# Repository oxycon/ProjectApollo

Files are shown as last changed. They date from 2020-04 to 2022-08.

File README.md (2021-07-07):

# ProjectApollo
This Github repository contains Designs/docs/software/PCB for Project Apollo (open source oxygen concentrator)

For more context behind the history/goals/motivation for this project please see our coverage in Helpful Engineering blog: 
- https://www.helpfulengineering.org/projects-news/project-spotlight-apollo-oxygen-concentrator/  

<b style='color:red'>Update</b>: check out our  presentation at RespiCon 2021! 
- https://github.com/oxycon/ProjectApollo/blob/master/docs/Project%20Apollo%20RespiCon%20v11.pdf

## Apollo v2 build instructions
- https://github.com/oxycon/ProjectApollo/blob/master/prototypes/Apollo%20v2/docs/Building%20instructions%20-%20prototype%20v2.pdf 

## Why
- Ventilators need oxygen! (typical FiO2 0.4 … 0.9)
- Oxygen generation is a big problem in developing countries. 
  - No established infrastructure. 
  - Oxygen bottles are expensive
- People are already looking at alternative (local) ways for producing oxygen
## What 
- Goal of the Apollo prototype = enabling people around the world to build the prototype as fast as possible
- Focus = Simplicity and speed of build 
- Final goal = Enable people to iterate and publish their own designs in the community
## How
- Follow the published build documentation
- Buy/source the materials (check out the BOM)
- Build the prototype
- Validate O2 concentration and flow. Use a good O2 and flow sensor. 
- Think about risk analysis and assessment: template for Apollo-derived design
- Document and iterate your own design. Publish your findings to the community! 

## Target 
- Output medical grade Oxygen ideally at 93% 
- Flow rate of 1-20 liters per minute (5 l/m being standard for oxygen therapy)

## Building instructions (prototype v2)
- Achieves O2 concentration out of the box: around 45% @ 5 liters/min (enough for less-critical ventilator use cases)
- Instructables-style (step-by-step) build instructions: https://github.com/oxycon/ProjectApollo/blob/master/prototypes/Apollo%20v2/docs/Building%20instructions%20-%20prototype%20v2.pdf 
- Bill of materials: https://github.com/oxycon/ProjectApollo/tree/master/prototypes/Apollo%20v2/BOM 

## Youtube videos
- Prototype v1 (old): https://www.youtube.com/playlist?list=PL34ykrB-qW7VGt1Hwd10Zb3s1eCDftkK8 
- Prototype v2 (latest): https://www.youtube.com/playlist?list=PL34ykrB-qW7X6d74_VnCFfBaVkm8pQXZK

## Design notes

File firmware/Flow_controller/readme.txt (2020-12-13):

This folder contains code/docs for the Flow Control with Oximeter project 

Slack channel: #hardware-oximeter-closed-loop-control discussed at Helpful Engineering

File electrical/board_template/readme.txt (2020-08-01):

Board template for Apollo boards (controller, valve driver board and sensor board)

PCB design template:
- 2-layer
- PC104 SAMTEC connector (4x26) 
- 88 mm x 88 mm = 7744 sq.mm (compatible with Eagle Freeware restrictions)
- bottom 2x26 pin row used for Apollo v4, top 2x26 pin row reserved for future use

Credit: 
- Base board template derived from the PCB design of HuskySat-1 satellite developed by University of Washington in collaboration with Raisbeck Aviation High School, Quick2space, AMSAT and others

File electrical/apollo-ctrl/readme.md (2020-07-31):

This is the circuit board for the main control circuit. The basic functions are:

 * Control all valves and fans
 * Monitor sensors
 * Monitor and alert for faults

The project is described and discussed in more detail here: https://docs.google.com/document/d/1zeXxTnBCQq67ddYeBdUPdo_KXUIRMmLPwQMJQMkbk8E/

The software used is Autodesk Eagle 9.

Please make your contributions on your own branches, as it's a nightmare merging changes to these files.

Please do not use default Eagle library components, add them to the local project .LBR file before adding them to the schematic. This ensures that everybody is using the same part and gives us the flexibility to fine tune the components.

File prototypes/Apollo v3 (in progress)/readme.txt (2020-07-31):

Apollo v3

Changes:
1) Control board (firmware/software)
	- please see the latest design from ..\firmware and ..\electrical
2) improved overall pneumatics: 3/8 piping for air intake, etc. 
3) improved zeolite (finer-grade 13X zeolite 20-40 instead of 4-8)

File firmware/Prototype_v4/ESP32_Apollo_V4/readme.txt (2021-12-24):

  ESP32 Oxygen Concentrator
 ===========================
 
This software is provided "as is" for educational purposes only. 
No claims are made regarding its fitness for medical or any other purposes. 
The authors are not liable for any injuries, damages or financial losses.

Use at your own risk!

License: MIT https://github.com/oxycon/ProjectApollo/blob/master/LICENSE.txt
For more information see: https://github.com/oxycon/ProjectApollo

------------------------------------------------------------------------------------

ESP32 Arduino install Video: https://www.youtube.com/watch?v=DgaKlh081tU&time_continue=61
  - Install Arduino IDE from https://www.arduino.cc/en/Main/Software
  - File => Preferences => Sketchbook location: {parent directory of this file, containing the "Libraries" directory, such as "root\ProjectApollo\firmware\Prototype_v4"}
  - File => Preferences => Additional Boards Manager URLs: https://dl.espressif.com/dl/package_esp32_index.json
  - Tools => Board: "xxx" => Boards Manager => ESP32
  - Tools => Board: "xxx" => ESP32 Arduino => "WEMOS LOLIN32" (or "ESP32 PICO Kit" if using the PICO board)
  - Tools => Serial Monitor => Baud: 115200

Install Library:
  - TFT_eSPI
  	!!! Edit Documents\Arduino\libraries\TFT_eSPI\User_Setup.h and configure ESP32 LCD SPI pins
  - TJpg_Decoder
  - ArduinoJson

Change WIFI credentials in Secrets.h

Note: force config change
- change #define CONFIG_MAGIC in Config.h

Control and Configuration:
There is an interactive command line interface that can be used with over the serial interface or TCP port 23.
Use telnet, PuTTY from https://putty.org or nc to connect using TCP.
Use Arduino IDE "tools=>Serial Monitor" or PuTTY from https://putty.org to connect using the USB serial port.

----------------------------------------------------------------------------------------------

  The ESP32 started randomly crashing
 =====================================

/home/runner/work/esp32-arduino-lib-builder/esp32-arduino-lib-builder/esp-idf/components/freertos/queue.c:1446 (xQueueGenericReceive)- assert failed!
abort() was called at PC 0x4008939b on core 1

Backtrace: 0x4008cf60:0x3ffbe690 0x4008d191:0x3ffbe6b0 0x4008939b:0x3ffbe6d0 0x400df875:0x3ffbe710 0x400d86cc:0x3ffbe730 0x400d6053:0x3ffbe750 0x400d60b5:0x3ffbe770 0x40080f89:0x3ffbe790 0x40081d95:0x3ffbe7b0 0x40085249:0x3ffbe7d0 0x4000bfed:0x3ffb1dd0 0x4008a7f1:0x3ffb1de0 0x40089ca4:0x3ffb1e00 0x400de844:0x3ffb1e30 0x400debcf:0x3ffb1e60 0x400d8859:0x3ffb1e80 0x400d88ad:0x3ffb1ea0 0x400d89bd:0x3ffb1ec0 0x400d7f3d:0x3ffb1ee0 0x400d81b8:0x3ffb1f10 0x400d8419:0x3ffb1f30 0x400d177b:0x3ffb1f50 0x400d59e9:0x3ffb1f70 0x400d4f7d:0x3ffb1f90 0x400e0fcd:0x3ffb1fb0 0x40089675:0x3ffb1fd0

0x4008cf60: invoke_abort at /home/runner/work/esp32-arduino-lib-builder/esp32-arduino-lib-builder/esp-idf/components/esp32/panic.c line 155
0x4008d191: abort at /home/runner/work/esp32-arduino-lib-builder/esp32-arduino-lib-builder/esp-idf/components/esp32/panic.c line 170
0x4008939b: xQueueGenericReceive at /home/runner/work/esp32-arduino-lib-builder/esp32-arduino-lib-builder/esp-idf/components/freertos/queue.c line 1446
0x400dfaf5: spiTransaction at C:\Users\caavenha\AppData\Local\Arduino15\packages\esp32\hardware\esp32\1.0.4\cores\esp32\esp32-hal-spi.c line 722
0x400d86bd: SPIClass::beginTransaction(SPISettings) at C:\Users\caavenha\AppData\Local\Arduino15\packages\esp32\hardware\esp32\1.0.4\libraries\SPI\src\SPI.cpp line 135
0x400d6058: valve_update_spi() at C:\Users\caavenha\AppData\Local\Temp\arduino_build_850040\sketch\Valve.cpp line 68
0x400d60cd: set_valves(unsigned char, unsigned char) at C:\Users\caavenha\AppData\Local\Temp\arduino_build_850040\sketch\Valve.cpp line 82
0x40080f89: concentratorISR() at C:\Users\caavenha\AppData\Local\Temp\arduino_build_850040\sketch\Concentrator.cpp line 27
0x40081d95: __timerISR at C:\Users\caavenha\AppData\Local\Arduino15\packages\esp32\hardware\esp32\1.0.4\cores\esp32\esp32-hal-timer.c line 88
0x4008a5c6: vTaskEnterCritical at /home/runner/work/esp32-arduino-lib-builder/esp32-arduino-lib-builder/esp-idf/components/freertos/tasks.c line 4190
0x4008b054: xTaskResumeAll at /home/runner/work/esp32-arduino-lib-builder/esp32-arduino-lib-builder/esp-idf/components/freertos/tasks.c line 2224
0x40089ca7: xEventGroupWaitBits at /home/runner/work/esp32-arduino-lib-builder/esp32-arduino-lib-builder/esp-idf/components/freertos/event_groups.c line 428
0x400de86c: i2cProcQueue at C:\Users\caavenha\AppData\Local\Arduino15\packages\esp32\hardware\esp32\1.0.4\cores\esp32\esp32-hal-i2c.c line 1279
0x400debf7: i2cWrite at C:\Users\caavenha\AppData\Local\Arduino15\packages\esp32\hardware\esp32\1.0.4\cores\esp32\esp32-hal-i2c.c line 1621
0x400d8881: TwoWire::writeTransmission(unsigned short, unsigned char*, unsigned short, bool) at C:\Users\caavenha\AppData\Local\Arduino15\packages\esp32\hardware\esp32\1.0.4\libraries\Wire\src\Wire.cpp line 133
0x400d88d5: TwoWire::endTransmission(bool) at C:\Users\caavenha\AppData\Local\Arduino15\packages\esp32\hardware\esp32\1.0.4\libraries\Wire\src\Wire.cpp line 158
0x400d89e5: TwoWire::endTransmission() at C:\Users\caavenha\AppData\Local\Arduino15\packages\esp32\hardware\esp32\1.0.4\libraries\Wire\src\Wire.cpp line 316
0x400d7f65: Adafruit_BME280::read24(unsigned char) at C:\Users\caavenha\Documents\Arduino\libraries\Adafruit_BME280_Library\Adafruit_BME280.cpp line 316
0x400d81e0: Adafruit_BME280::readTemperature() at C:\Users\caavenha\Documents\Arduino\libraries\Adafruit_BME280_Library\Adafruit_BME280.cpp line 407
0x400d8441: Adafruit_BME280::readHumidity() at C:\Users\caavenha\Documents\Arduino\libraries\Adafruit_BME280_Library\Adafruit_BME280.cpp line 468
0x400d177f: Bme::run() at C:\Users\caavenha\AppData\Local\Temp\arduino_build_850040\sketch\BME280.cpp line 32
0x400d59ed: sensor_run() at C:\Users\caavenha\AppData\Local\Temp\arduino_build_850040\sketch\SensorManager.cpp line 89
0x400d4f81: loop() at C:\Repos\ProjectApollo\firmware\Prototype_v4\ESP32_Apollo_V4/ESP32_Apollo_V4.ino line 69
0x400e0ff5: loopTask(void*) at C:\Users\caavenha\AppData\Local\Arduino15\packages\esp32\hardware\esp32\1.0.4\cores\esp32\main.cpp line 19
0x40089675: vPortTaskWrapper at /home/runner/work/esp32-arduino-lib-builder/esp32-arduino-lib-builder/esp-idf/components/freertos/port.c line 143

It is possible that it is not safe to call the SPI from the timer ISR in Concentrator.cpp
Essentially SPI_MUTEX_LOCK(); in esp32-hal-spi.c asserts sometimes. One possiblity could be to use software SPI for the valves.

A search also revealed:
https://github.com/espressif/arduino-esp32/issues/149 : hardware SPI is slower than software SPI by maybe a factor of 3 

For the time being SPI locks need to be disabled:
C:\Users\<user>\AppData\Local\Arduino15\packages\esp32\hardware\esp32\1.0.4\cores\esp32\esp32-hal-spi.c
#define CONFIG_DISABLE_HAL_LOCKS 1

----------------------------------------------------------------------------------------------

Type help or ? to get a list of CLI commands.

led <0|1|on|off|true|false>            Set LED state
valve <n> [0|1|on|off|true|false]      Set or get valve state
valve-drivers [count]                  Number of installed DRV-8806 valve driver chips
concentrator [0|1|on|off|true|false]   Enable or disable concentrator stage
stage-duration <stage> [miliseconds]   Set or get the duration of a specifc stage
stage-durations [miliseconds] [...]    Set or get the stage durations
stage-valves <stage> [valves]          Set or get stage valve state bit-map
stage-valve-mask <mask>                Set or get bit-masks of which valves should switch during stages
oxygen                                 Get results of last oxygen sensor measurements
pressure                               Get results of last pressure sensor measurements
humidity                               Get results of last humidity sensor measurements
temperature                            Get results of last temperature sensor measurements
color                                  Get results of last color sensor measurements
errors                                 Get error log
adr-ambient [address]                  Set or get the address of the ambient humidity, temperture, pressure sensor
adr-intake [address]                   Set or get the address of the intake humidity, temperture sensor
adr-desiccant [address]                Set or get the address of the desiccant humidity, temperture sensor
adr-output [address]                   Set or get the address of the output humidity, temperture sensor
adr-in-pressure [address]              Set or get the address of the intake pressure sensor
adr-color [address]                    Set or get the address of the color sensor
adr-out-pressure [address]             Set or get the address of the output pressure sensor
data-log [0|1|on|off|true|false]       Enable or disable concentrator data logging
cycle-stats [0|1|on|off|true|false]    Enable or disable cycle stats logging
stats [0|1|on|off|true|false]          Enable or disable long term stats logging
debug [0|1|on|off|true|false]          Enable or disable debug logging
wifi-enabled [0|1|on|off|true|false]   Enable or disable WIFI on next restart
ssid                                   Set or get WIFI SSID
wifi-password                          Set or get WIFI password
wifi-ip                                Set or get fixed WIFI IP address
dns                                    Set or get fixed WIFI DNS
gateway                                Set or get fixed WIFI gateway
subnet                                 Set or get fixed WIFI subnet
time-format                            Set or get format for time representation
date-format                            Set or get format for date representation
save                                   Save current configuration to FLASH
load                                   Restore configuration from FLASH
config                                 Return configuration as JSON
data                                   Return current sensor data as JSON
ip                                     Get local-IP address
mac                                    Get MAC address
time                                   Get current time
timezone [time zone]                   Set or get the local time zone
brighness [value]                      Set or get the display brightness 0 to 100
restart                                Restart the controller
help                                   Print help
?                                      Print help

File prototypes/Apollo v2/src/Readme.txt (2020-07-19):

Please see ../../../firmware/Prototype_v2

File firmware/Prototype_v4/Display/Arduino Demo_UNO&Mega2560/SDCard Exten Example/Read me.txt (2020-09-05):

Attention:
"SDCard Exten Example" only support the Arduino UNO board,not support the Mega2560,Because they use different SPI bus.

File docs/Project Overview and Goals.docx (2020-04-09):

Project Apollo Project Overview

DIY Oxygen Concentrator Project

Author: Adi Oltean, Jack Gallagher, Eric H Revision: 22nd March 2020

Working copy available at: https://drive.google.com/drive/folders/1AWvZsK41v0T8z20f_-QFAzTxI99lZbBv?ths=true

Goal 2

Justification 2

Assumptions 2

Project Timeline 2

Requirements 3

Useful links 3

Goal

The goal is to create extremely detailed DIY instructions for the creation of an Open Source Oxygen Concentrator. This should be concise and clear so it can be followed by those with little to no previous experience in building these types of systems.

The target price is less than $100 although this may be infeasible once development and prototypes are created.

Justification

- In the Helpful Engineering Round 1 Peer review this project was ranked 14th out of 26

proposals to make it to that stage. - It was ranked in the top 5 of the hardware projects. - It was ranked by Anaesthesiologists as “Hugely important” with a comment of “Lack of

O2 pipeline supply”

Assumptions

Note: Any assistance confirming or denying any assumptions would be appreciated as expert knowledge has not been available to date.

- Access to oxygen-rich air is critical to many medical facilities across the globe given that

we are running out of beds in many affected areas by COVID-19 [1], [2] - Additionally, according to the interviewed Seattle doc, 2⁄3 of hospitalized patients didn’t require much more care than o2 therapy, so any way to rapidly scale out concentrator production can probably take a large load off of hospitals. - There is no clear guideline on the percentage Oxygen and flow rate required. Target

Oxygen Concentration will be 93%. Acceptable range will be 70% to 100%. Target Oxygen Flow will be 5 litres per minute. The Acceptable range will be 1 to 20 litres per minute.

Project Timeline

- Project start date: March 12nd 2020 - Plan to complete build of prototype V1 by March 22nd. - Plan testing of prototype V1 from March 23rd to March 25th. - Community feedback in the week of March 26th to March 30th. - Publish schematics/instructions: April 4th. - Publish educational videos: April 11th.

Requirements

- Target Oxygen Concentration will be 93%. Acceptable range will be 70% to 100%. - Target Oxygen Flow will be 5 litres per minute. The Acceptable range will be 1 to 20

litres per minute. - Long-running (>1.5 years). - High dependability. - Simple design:

- Eliminate anything not strictly needed in the initial prototype. - Example: No built-in compressor. Instead it should work with a variety of external

compressors, some which can generate impurities such as oil mist or water vapors (common problems with all compressors) - Should be possible to construct from household or freely available materials. - Detail of suitable mechanism to ensure molecular sieve is not restricted from oil (from

compressor) to be provided. - Easy to maintain (i.e. easy to tear down, fix and replace drying silica beads or zeolite

beads etc.) - Should not require calibration or complex sensors.

Useful links

- Project GitHub: https://github.com/oxycon/ProjectApollo/projects - Project Google Drive:

https://drive.google.com/drive/folders/1AWvZsK41v0T8z20f_-QFAzTxI99lZbBv?ths=true - Project Slack Channel: https://helpfulengineering.slack.com/archives/C0105E2T0UB

END

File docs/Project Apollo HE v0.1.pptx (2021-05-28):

## Product: Apollo O2 Concentrator

Description
O2 Concentrator: Simple, reliable design (zeolite-based PSA system). Flexible, open source, using off-the-shelf materials
Differentiators
Very low cost (aspirational target = $250 for 15 liters/min @ 90%) – current BOM cost range on prototypes have been $260-450 with retail ordered parts and components (not including cost of compressor and oxygen sensor) Safety & Usability: Detect all failure scenarios, User experience and maintainability. Clear, actionable error messages, Alarm sensors Self-regulating: Patient sensor/data feedback loop Touch screen for diagnostic messages, medical-grade buzzer, large 2.5" OLED screen, localizable messages in any locale/character set Open source, modular PCB design. Works with a variety of sen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
Product Quality Standards and Prototype Readiness
Compatible and adaptable with the Indian Supply Chain driven BOM Compliant with new Indian Govt. guidelines on O2 Concentrator Feature sets Can be assembled in a lead time of 4-5 hours given availability of parts

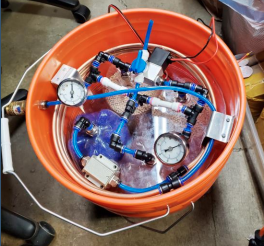
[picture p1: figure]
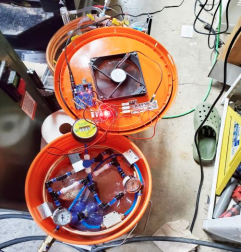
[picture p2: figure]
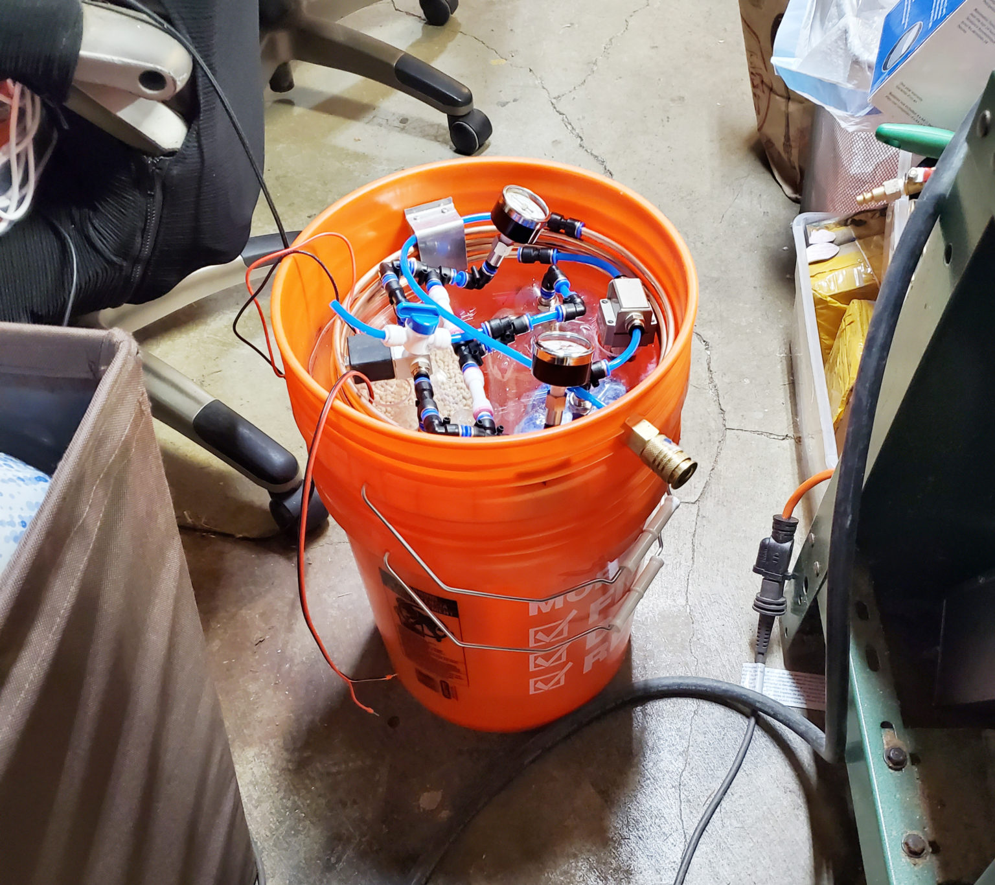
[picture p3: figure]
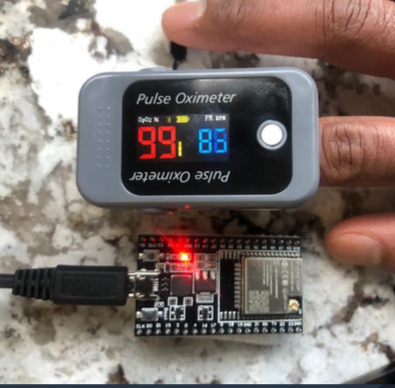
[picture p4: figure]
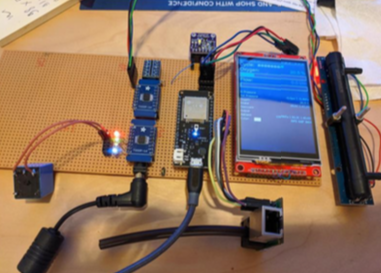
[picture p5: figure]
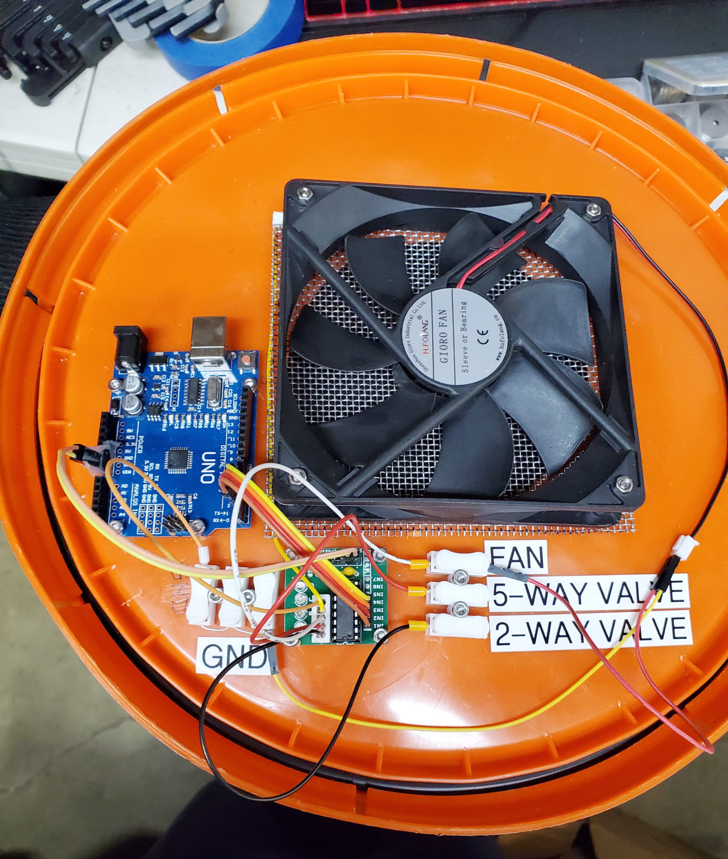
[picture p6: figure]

## Product: Apollo O2 Concentrator Key Advantages for an Indian Context

- Compliant design: Meets recent government guidelines on O2 Concentrator design features and capabilities
- Supply Chain Resilience: open-source, modular solution. Critical parts such as HEPA filters, silica gel, medical-grade oil free compressor and zeolite can be sourced locally, or anywhere with minimal re-testing required. Rapid assembly.
- Technology transfer: Enable Indian manufacturing participants to build and improve upon locally for Indian climactic conditions against a reference design
- Trust through Telemetry: Quality, safety, and effectiveness will be transparently trustworthy through direct measurement rather than design perfection. Building on direct, cloud-enabled, IoT-enabled measurement of all relevant performance characteristics we already have (https://github.com/PubInv/ventmon-ventilator-inline-test-monitor), will provide quality and safety visibility on each device implementation, and as oxygen concentrators are used and reused on multiple patients. Trust through telemetry provides maximum confidence when making minor part changes required by stressed supply chains.
- Rapid manufacture, low cost, scalable across Indian climactic contexts

## Product: Apollo O2 Concentrator Engineering Design Partners

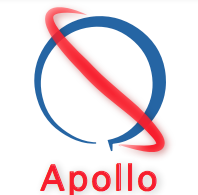
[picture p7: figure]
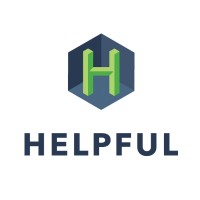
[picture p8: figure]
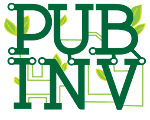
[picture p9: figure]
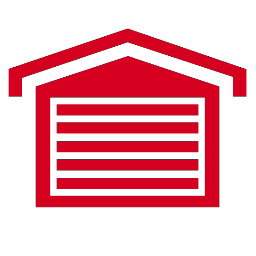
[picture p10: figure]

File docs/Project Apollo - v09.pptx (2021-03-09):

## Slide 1

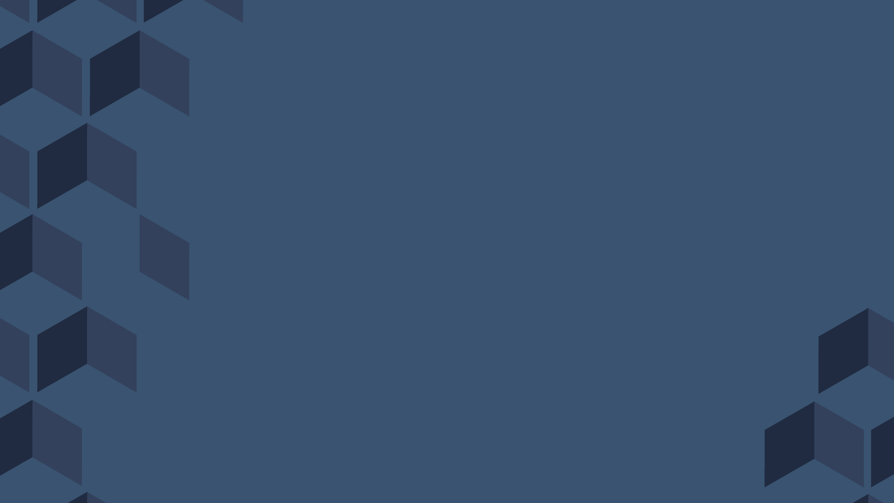
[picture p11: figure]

Project Apollo

An open source oxygen concentrator
http://project-apollo.org
#project-oxygen-concentrator

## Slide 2

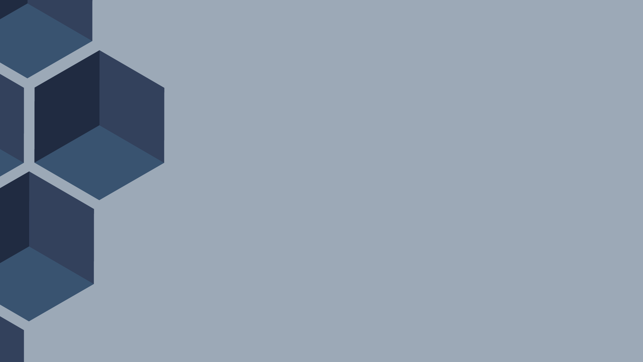
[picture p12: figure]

Project Apollo

Why
  - O2 needed for ventilators, oxygen therapy
    - Typical FiO2 0.3 … 0.5, up to 1
  - Oxygen generation is a big problem in developing countries
    - No established infrastructure
    - Oxygen bottles are expensive
  - People are already looking at alternative (local) ways for producing and delivering oxygen

https://www.economist.com/graphic-detail/2021/03/09/hospitals-are-running-out-of-oxygen-to-treat-covid-19-patients
https://www.cidrap.umn.edu/news-perspective/2021/03/who-sounds-alarm-over-covid-linked-oxygen-crisis
https://apnews.com/article/oxygen-crisis-africa-latin-america-eb0d2731a8613c1ae218db7d32a227a6

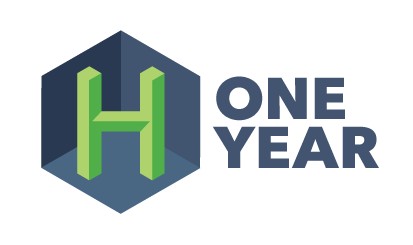
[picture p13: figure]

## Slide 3

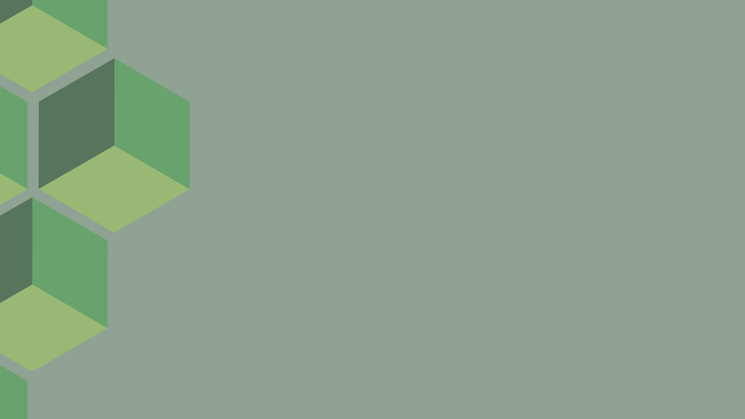
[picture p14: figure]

Project Apollo

What is it
  - Goal = enabling people around the world to build the prototype ASAP
  - Focus = Simplicity and speed of build
    - Simple, reliable design (zeolite-based PSA system)
    - Flexible, open source, off-the-shelf materials
    - Very low cost (aspirational target = $200 for 15 liters/min @ 80%)
  - Final goal = Enable people to iterate and publish their own designs in the community

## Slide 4

Project Apollo v2

How to build it
  - Follow the published build documentation (https://github.com/oxycon/ProjectApollo/blob/master/Prototype%20oxygen%20concentrator/docs/v2/Building%20instructions%20-%20prototype%20v2.pdf)
  - Buy/source the materials (check out the BOM (https://github.com/oxycon/ProjectApollo/tree/master/Prototype%20oxygen%20concentrator/BOM/v2))
  - Build the prototype
  - Validate O2 concentration and flow. Use a good reference O2 and flow sensor for calibration
Multiple iterations/variants have been built
  - O2 concentration 45 … 70%, 5 lpm

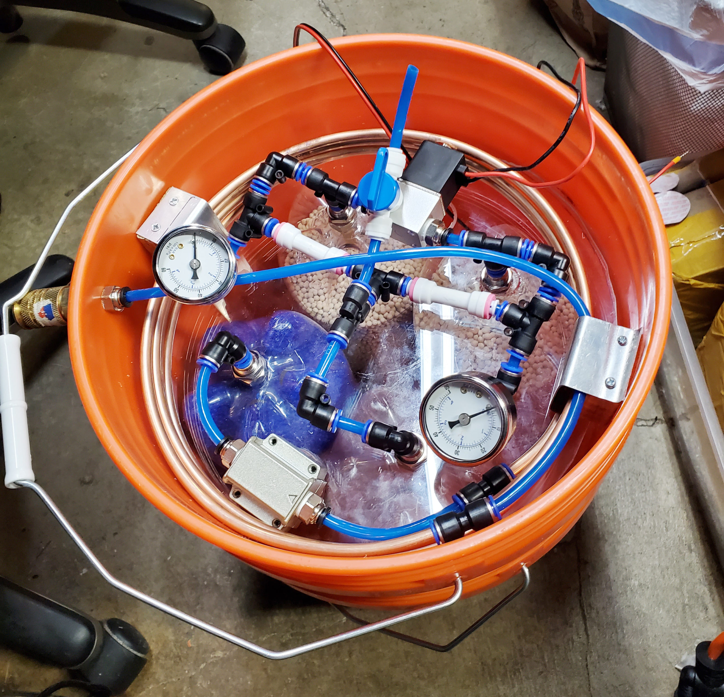
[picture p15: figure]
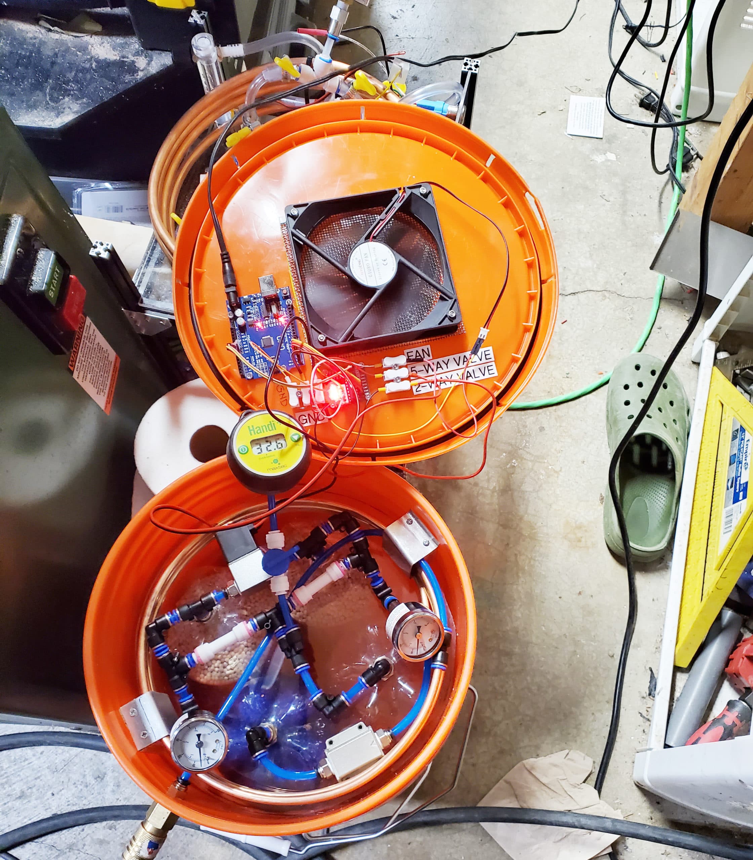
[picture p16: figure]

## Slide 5

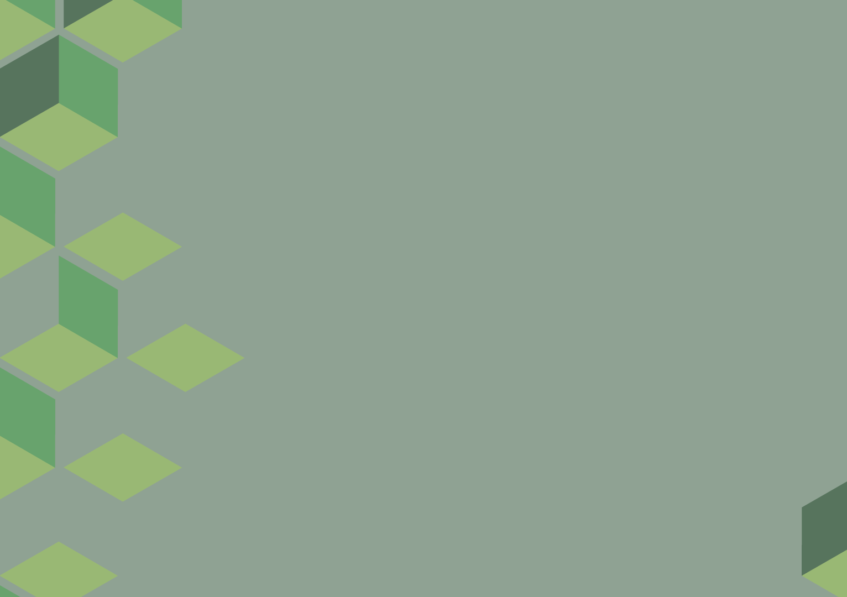
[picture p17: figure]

Project Apollo v4

Apollo v4
Focus = medical device
Safety: detect all failure scenarios
Ease of use: User experience and maintainability. Clear, actionable error messages
Self-regulating: Patient sensor/data feedback loop
Control box
Touch screen for diagnostic messages, medical-grade buzzer
Open source, modular PCB design. Works with a variety of sensors
Self-tuning: valve timing, auto-adjusts to changes in compressed air input pressure, machine learning
Integration with SpO2 oximeter Bluetooth sensor
Cloud data integration for patient monitoring
Self-contained enclosure
Built-in compressor
Full focus on thermals, airflow, noise reduction
Collaborations
Funding: Quick2space.org
Volunteers: Helpful Engineering, Microsoft Garage, Public Invention
Documentation, code
http://project-apollo.org

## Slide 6

Project Apollo v4

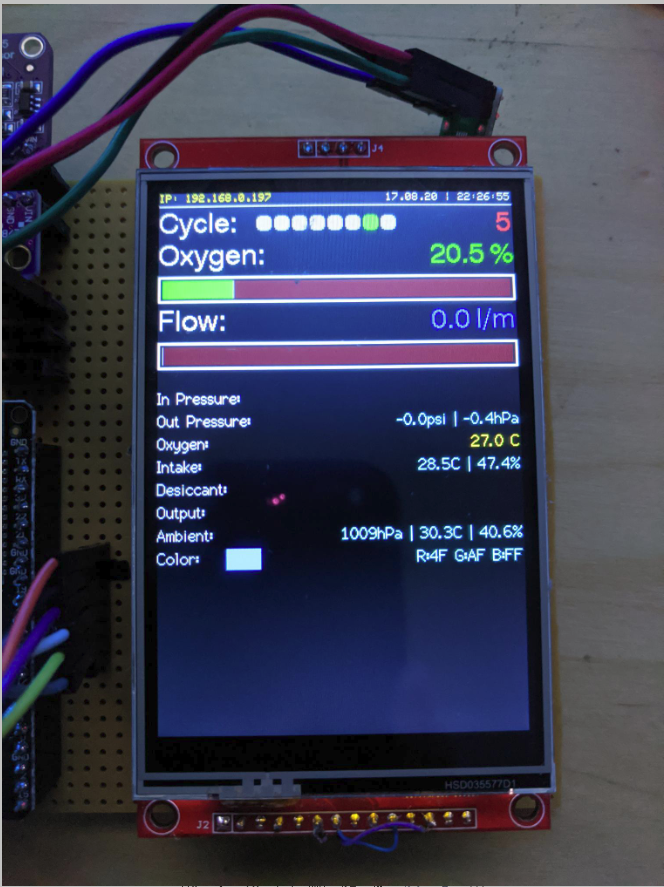
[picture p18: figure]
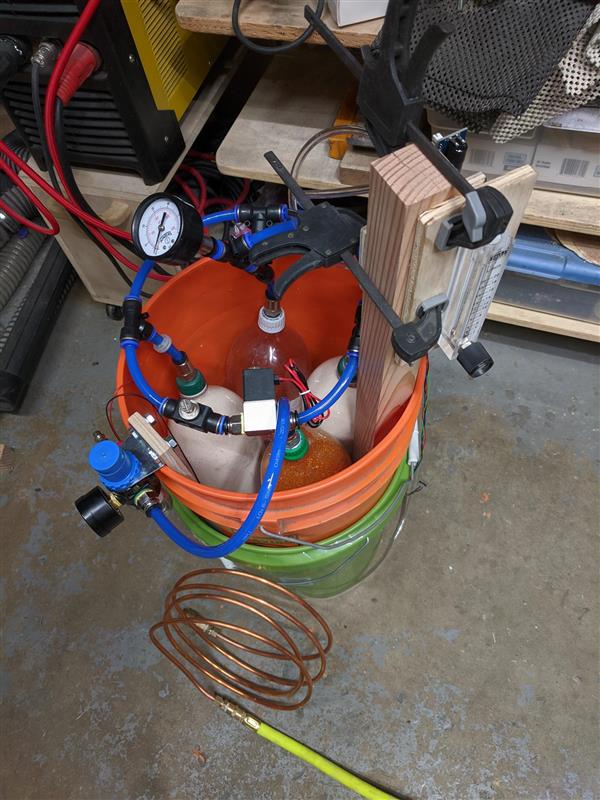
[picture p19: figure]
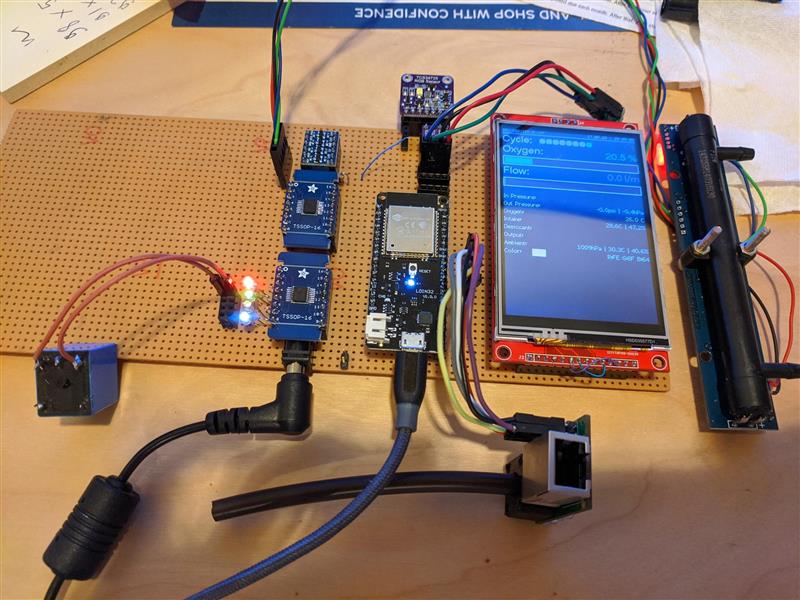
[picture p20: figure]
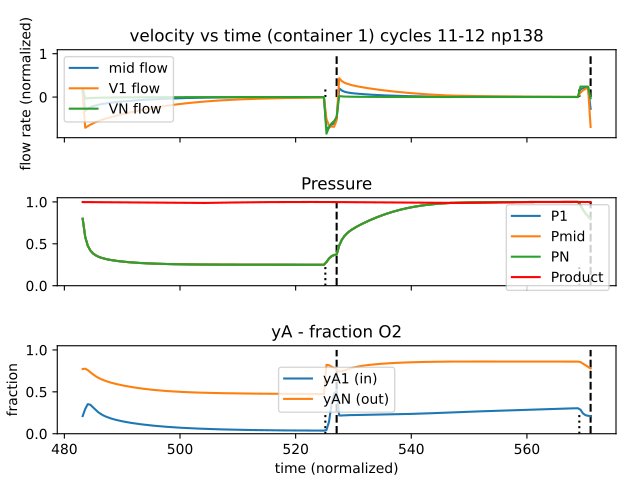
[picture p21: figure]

http://project-apollo.org

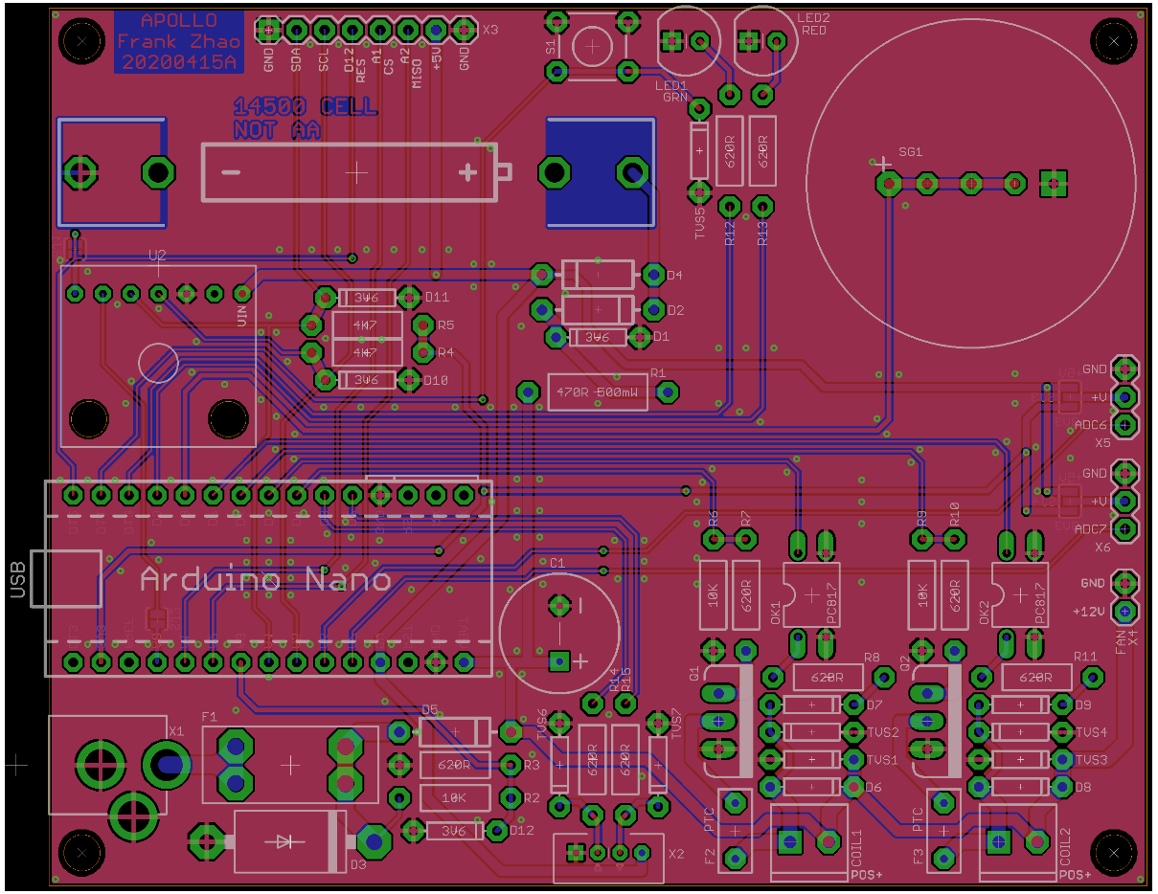
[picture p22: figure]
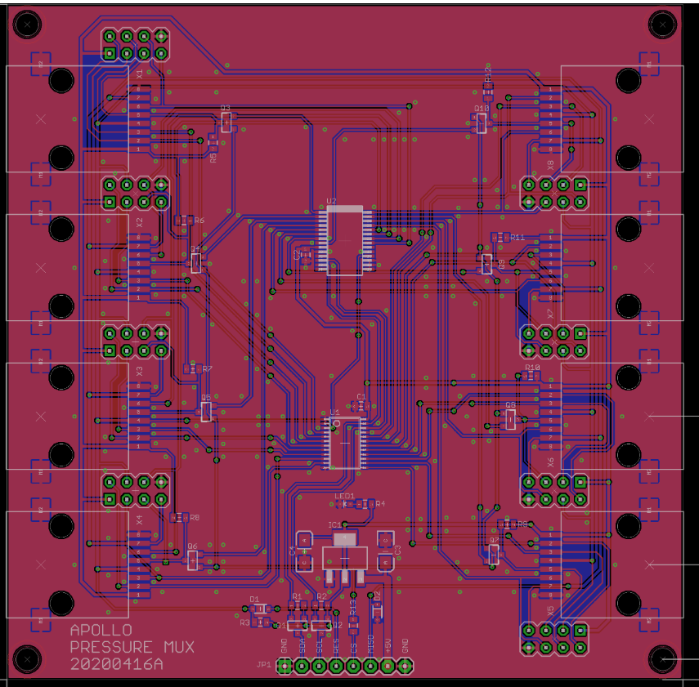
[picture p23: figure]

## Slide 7

Thank you!

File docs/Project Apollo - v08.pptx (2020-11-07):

## Apollo Control Box

  - Goal = Self-contained control box
    - Focus
      - Safety: detect all failure scenarios
      - Ease of use: User experience and maintainability. Large (3.5”) touch screen for diagnostic messages, medical-grade buzzer
    - Can drive with PSA-based O2 concentrator (Oxikit, PIOC, Apollo reference O2 concentrator)
      - Open source, modular PCB design. Works with a variety of sensors
    - Self-tuning AI
      - learning mode for adjusting valve timing, auto-adjusts to changes in compressed air input pressure
    - Continuous and pulse mode of operation
      - Adjust PSA operational cycle in sync with patient breathing
      - Pulse mode = key to greatly reduces compressor size and power consumption
  - Patient sensor/data integration
    - O2 flow regulation: adjust O2 flow in response to oximeter readings
      - SpO2 oximeter Bluetooth sensors
      - Breathing rate detection through pressure sensors and flow rate measurement
    - GTS/Teladoc integration
      - push medical data to the cloud for doctors to remotely monitor patients)
  - Integration
    - Oxikit: proportional valve flow control, GTS/Teladoc integration, Bluetooth oximeter
    - PIOC, Oxikit: control box
    - LifeMech – ventilator integration (TBD)
  - Status
    - v1..v3 designs published and tested, with Apollo O2 concentrator reference design
    - Apollo control box: Working on v4 (ETA November/December 2020 for first prototypes)
    - Pursuing GTS/Teladoc prototyping with Oxikit

## PSA/Ventilator integration points

- Goal
  - Unified solution?
- Requirements
  - Breathing rate detection
    - Ventilator can provide that info
    - Enables efficient pulse mode operation at PSA concentrator level
  - Flow regulation
    - Adjusts O2 concentration dynamically by adjusting PSA timings
    - Oximeter pulse reading (Bluetooth)
  - GTS/Teladoc integration
    - Patient data (SpO2 data)

## Prototypes


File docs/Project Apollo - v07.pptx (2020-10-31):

## Project Apollo

Why
  - Ventilators need oxygen! (typical FiO2 0.3 … 0.5)
  - Oxygen generation is a big problem in developing countries
  - People are already looking at alternative (local) ways for producing oxygen
Apollo Control Box v4
  - Universal control box
    - Should work with any PSA-based O2 concentrator
  - Focus
    - Safety: detect all failure scenarios
    - Ease of use: User experience and maintainability. Clear, actionable error messages
  - What is it = Self-contained control box
    - Large (3.5”) touch screen for diagnostic messages, medical-grade buzzer
    - Open source, modular PCB design. Works with a variety of sensors
    - New: self-tuning (valve timing, auto-adjusts to changes in compressed air input pressure, machine learning)
  - Patient sensor/data integration (optional)
    - SpO2 oximeter Bluetooth sensors, detecting breathing pattern to optimize O2 flow
    - Continuous and pulse mode of operation. Pulse mode = key to greatly reduces compressor size and power consumption
  - Status
    - v1..v3 designs published and tested, with Apollo O2 concentrator reference design
    - Working on v4 (ETA November 2020 for first prototypes)
Collaborations
  - Helpful Engineering, Public Invention, Oxikit, Microsoft Garage, Quick2space.org
Documentation, code
  - http://project-apollo.org

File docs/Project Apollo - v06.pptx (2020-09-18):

## Project Apollo

Why
  - Ventilators need oxygen! (typical FiO2 0.3 … 1)
  - Oxygen generation is a big problem in developing countries.
    - No established infrastructure.
    - Oxygen bottles are expensive
  - People are already looking at alternative (local) ways for producing oxygen
What it is
  - Goal of the Apollo prototype = enabling people around the world to build the prototype ASAP
  - Focus = Simplicity and speed of build
    - Simple, reliable design (zeolite-based PSA system)
    - Flexible, open source, off-the-shelf materials
    - Very low cost (aspirational target = $100 for 5 liters/min @ 90%)
  - Final goal = Enable people to iterate and publish their own designs in the community
How to build it
  - Follow the published build documentation (https://github.com/oxycon/ProjectApollo/blob/master/Prototype%20oxygen%20concentrator/docs/v2/Building%20instructions%20-%20prototype%20v2.pdf)
  - Buy/source the materials (check out the BOM (https://github.com/oxycon/ProjectApollo/tree/master/Prototype%20oxygen%20concentrator/BOM/v2))
  - Build the prototype
  - Validate O2 concentration and flow. Use a good reference O2 and flow sensor for calibration
  - Think about risk analysis and assessment: template for Apollo-derived design (https://github.com/oxycon/ProjectApollo/blob/master/docs/Ops%20Risk%20Analysis_Risk%20Assmt%20Iss01%20(Apollo%20v01).xlsx)
  - Document and iterate your own design. Publish your findings to the community!
Collaborations
  - Helpful Engineering, Public Invention, Oxikit, Microsoft Garage , Quick2space.org
Documentation
  - http://project-apollo.org


## Project Apollo – latest progress

- Next version (Apollo v4) coming soon
  - Focused on safety, user experience and maintainability
  - O2 compatible materials in the oxygen path
  - Dedicated PCB controller board, sensor integration, valve operational sensing
    - 3” TFT touch screen for diagnostic messages, medical-grade buzzer
    - Auto-tuning (valve timing, auto-adjusts to changes in compressed air input pressure)
  - Integration with SpO2 oximeter Bluetooth sensors
    - Pulse mode prototype
- Status
  - Mechanical design (collaboration with Public Invention)
    - Focus on FDA approval, sourcing deals @ volume and manufacturing
    - Please see project “Oxygen Concentrator” from Public Invention (@Ben Coombs)
  - Software prototypes for Apollo v4 – working
    - Simulation software
      - “device in the loop’ optimization strategies – tested and delivering close to theoretical
    - Can control Apollo for O2 generation and basic optimization
    - WiFi and Bluetooth integration TBD
  - Hardware design
    - Sensor selection - Sensors for pressure, humidity, temperature – selected and tested
    - Valve board – schematic in review, PCB in progress
    - Controller board – schematic in review, PCB in progress
    - Sensor board – schematic in progress, PCB in progress (inspired from Apollo v3)

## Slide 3

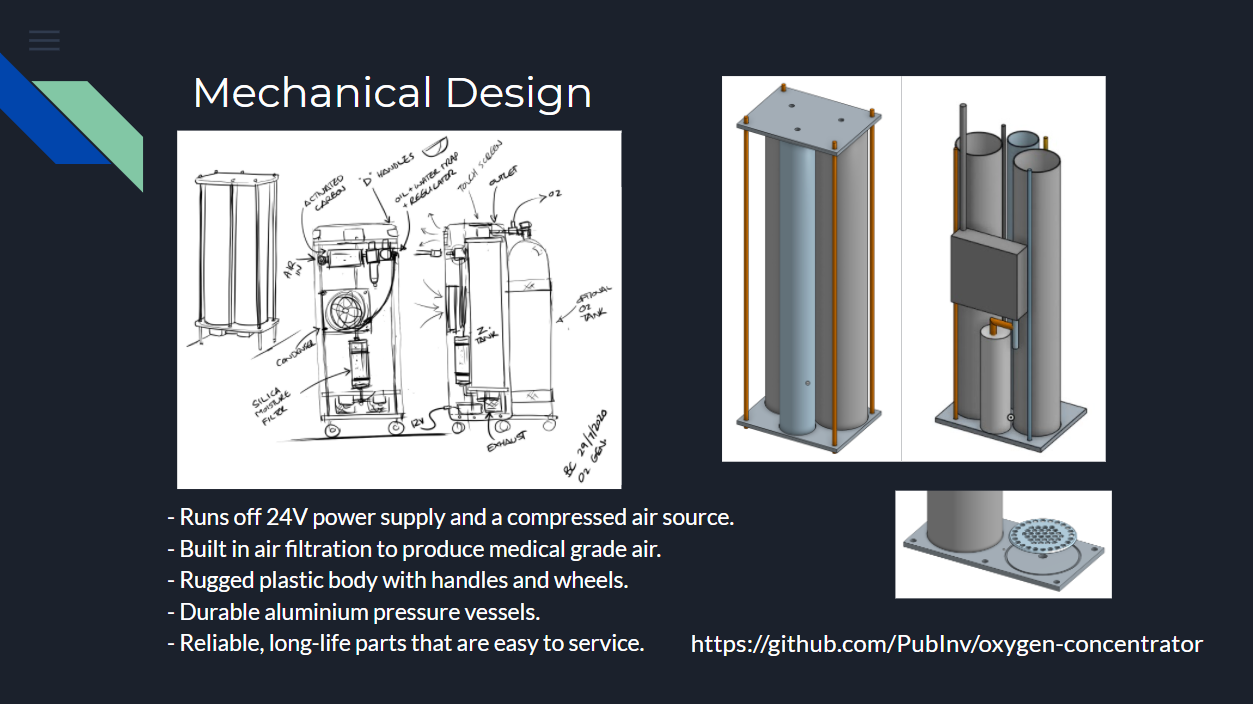
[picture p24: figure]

## Prototyping effort – electronics, software


## Conclusion

- Apollo
  - Open source oxygen concentrator with focus on low-cost
  - When Apollo v4 comes out we encourage everyone to build one!
- Please visit us at
  - http://project-Apollo.org
    - Track here our progress on Github for designs, PCBs and software
  - http://HelpfulEngineering.org
    - Slack channel = #project-oxygen-concentrator
  - www.pubinv.org
    - Public Invention main website

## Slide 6


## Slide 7


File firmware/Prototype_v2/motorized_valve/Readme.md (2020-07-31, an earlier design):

# Overview

This simple Arduino example demonstrates driving a stepper motor using a combination of PCA9685 I2C multiplexer board and an ULN2003 Darlington driver. 

One single PCA9685 board can drive up to 4 stepper motors. The example can be easily extended to drive a very large number of stepper motors using one Arduino board, simply by chaining multiple PCA9685 boards.

We demonstrate this using a BYJ48 stepper motor which can be driven straight from the USB bus. 

All components involved are fairly inexpensive (total cost < $15-$20). 

# Mechanical components
- Heavy Duty Brass Replacement Control Needle Valve 1/4" Female NPT X 1/4" Female NPT [link](https://www.amazon.com/Litorange-Replacement-Control-Needle-Connection/dp/B07YFR72JP/). You need to unscrew the brass knob (held in place with epoxy/thread-lock resin which can be molten using a lighter). After unscrewing you have a 1/4" brass stem on which the coupler can be mounted.
- An 5mm to 6.35 mm (1/4") motor stepper coupler or equivalent [link](https://www.amazon.com/gp/product/B07YDGZJCZ/)
- A DIY structure that will hold the motor and the needle valve together in place

# Electronic components
- Arduino Uno or equivalent
- ULN2003 board
- PCA9685 board
- Stepper motor (BYJ48). 5 mm shaft. 
- Breadboard + jumper wires
- 5V power supply, strong enough to drive the stepper motors (< 1A?)

# Connections
- from Arduino Uno to PCA9695
  - 5V    ->    Vcc 
  - GND   ->    GND
  - SCL   ->    SCL
  - SDA   ->    SDA
  - Vin   ->    Power V+ (or from standalone external 5V power source)
  - GND   ->    Power GND

- from Arduino Uno to ULN2003 
  - Vin   ->    Power + (5..12V)	(or from standalone external 5V power source)
  - GND   ->    Power - 
       
- from PCA9685 to ULN2003 board
  - PWM pin 0   ->    IN 1
  - PWM pin 1   ->    IN 2
  - PWM pin 2   ->    IN 3
  - PWM pin 3   ->    IN 4

- from ULN2003 to BYJ48 stepper motor
  - Use the standard 5-pin connector with the default wiring

# Notes
- The stepper motor rotates using default power from USB assuming a high-power USB port (1A minim)
- If you want to drive bigger motors or multiple motors you can supply 5V using an external power source. The ground still needs to be kept common.
- There is no code currently for endstop detection. You would need to control the total travel time in software.

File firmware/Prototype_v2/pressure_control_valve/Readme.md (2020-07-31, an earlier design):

# Overview

This simple Arduino example demonstrates driving a stepper motor using a combination of PCA9685 I2C multiplexer board and an ULN2003 Darlington driver. 

One single PCA9685 board can drive up to 4 stepper motors. The example can be easily extended to drive a very large number of stepper motors using one Arduino board, simply by chaining multiple PCA9685 boards.

We demonstrate this using a BYJ48 stepper motor which can be driven straight from the USB bus. 

All components involved are extremely inexpensive. 

# Components
- Arduino Uno or equivalent
- ULN2003 board
- PCA9685 board
- Stepper motor (BYJ48)
- Breadboard + jumper wires

# Connections
- from Arduino Uno to PCA9695
  - 5V    ->    Vcc 
  - GND   ->    GND
  - SCL   ->    SCL
  - SDA   ->    SDA
  - Vin   ->    Power V+
  - GND   ->    Power GND

- from Arduino Uno to ULN2003
  - Vin   ->    Power + (5..12V)	
  - GND   ->    Power - 
       
- from PCA9685 to ULN2003 board
  - PWM pin 1   ->    IN 1
  - PWM pin 2   ->    IN 2
  - PWM pin 3   ->    IN 3
  - PWM pin 4   ->    IN 4

- from ULN2003 to BYJ48 stepper motor
  - Use the standard 5-pin connector with the default wiring

# Notes
- the stepper motor rotates using default power from USB assuming a high-power USB port (1A minim)

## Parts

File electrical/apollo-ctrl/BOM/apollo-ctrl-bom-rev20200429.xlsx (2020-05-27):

Qty | Des | Name | Value | Rating | Footprint | Digi-Key
1 | C1 | capacitor, electrolytic | 47uF | 25V | TH, 5mm pitch, 11mm dia | https://www.digikey.com/short/zzb82b
2 | COIL1, COIL2 | terminal block |  |  | TH, 3.5mm | https://www.digikey.com/short/zzb8w4
4 | D1, D10, D11, D12 | diode, zener | 3.6V | 500mW | TH, DO-35 | https://www.digikey.com/short/zzb8n2
3 | D2, D4, D5 | diode, schottky |  |  | TH, DO-15 | https://www.digikey.com/short/zzb8vq
1 | D3 | diode, zener | 13V | 5W | TH, DO-201 | https://www.digikey.com/product-detail/en/central-semiconductor-corp/CZ5350B-TR-PBFREE/1514-CZ5350BTRPBFREECT-ND/5324340
4 | D6, D7, D8, D9 | diode | 1N4148 |  | TH, DO-35 | https://www.digikey.com/short/zzb81w
1 | F1 | fuse holder |  |  | TH | https://www.digikey.com/product-detail/en/keystone-electronics/3568/36-3568-ND/2137306
1 | F1 | fuse | 3A |  |  | https://www.digikey.com/short/zzbj7z
1 | LED1 | LED | green |  | TH, 5mm | https://www.digikey.com/short/zzbjb4
1 | LED2 | LED | red |  | TH, 5mm | https://www.digikey.com/short/zzbjb5
2 | F2, F3 | fuse, PTC |  |  |  | https://www.digikey.com/product-detail/en/littelfuse-inc/RHEF070/RHEF070HF-ND/5029792
2 | OK1, OK2 | optocoupler | 817 |  | TH, DIP | https://www.digikey.com/short/zzbj33
2 | Q1, Q2 | MOSFET | N-chan | 1A, 20V | TO-220 | https://www.digikey.com/short/zzbjq4
1 | R1 | resistor | 470Ω | 500mW | TH | https://www.digikey.com/short/zzbjjh
7 | TVS | diode, TVS | 16V |  | DO-15 | https://www.digikey.com/product-detail/en/littelfuse-inc/P6KE16CA/P6KE16CALFCT-ND/407666
1 | SG1 | buzzer | 3V |  | TH | https://www.digikey.com/product-detail/en/pui-audio-inc/AI-3035-TWT-3V-R/668-1204-ND/1745457
1 | X1 | power jack |  |  | TH | https://www.digikey.com/product-detail/en/cui-devices/PJ-002AH/CP-002AH-ND/408446
8 | R7, R8, R10, R11, R12, R13, R14, R15 | resistor | 620Ω | 0.25W | TH | https://www.digikey.com/short/zzbjht
2 | R4, R5 | resistor | 4.7kΩ | 0.25W | TH | https://www.digikey.com/short/zzbjhq
3 | R2, R6, R9 | resistor | 10kΩ | 0.25W | TH | https://www.digikey.com/short/zzbjhj

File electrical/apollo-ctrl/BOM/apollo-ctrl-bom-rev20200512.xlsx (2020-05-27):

Qty | Des | Name | Value | Rating | Footprint | Digi-Key Filter | Digi-Key Item
1 | C1 | capacitor, electrolytic | 47uF | 25V | TH, 5mm pitch, 11mm dia | https://www.digikey.com/short/zzb82b | https://www.digikey.com/product-detail/en/nichicon/UVZ1J101MPD/493-1355-ND/589096
2 | COIL1, COIL2 | terminal block |  |  | TH, 3.5mm | https://www.digikey.com/short/zzb8w4 | https://www.digikey.com/product-detail/en/phoenix-contact/1984617/277-1721-ND/950849
4 | D1, D10, D11, D12 | diode, zener | 3.6V | 500mW | TH, DO-35 | https://www.digikey.com/short/zzb8n2 | https://www.digikey.com/product-detail/en/on-semiconductor/BZX79C3V6/BZX79C3V6-ND/977916
3 | D2, D4, D5 | diode, schottky |  |  | TH, DO-15 | https://www.digikey.com/short/zzb8vq | https://www.digikey.com/product-detail/en/smc-diode-solutions/SB240TA/1655-1519-1-ND/6022964
1 | D3 | diode, zener | 13V | 5W | TH, DO-201 |  | https://www.digikey.com/product-detail/en/central-semiconductor-corp/CZ5350B-TR-PBFREE/1514-CZ5350BTRPBFREECT-ND/5324340
4 | D6, D7, D8, D9 | diode | 1N4148 |  | TH, DO-35 | https://www.digikey.com/short/zzb81w | https://www.digikey.com/product-detail/en/on-semiconductor/1N4148TR/1N4148FSCT-ND/9356376
1 | F1 | fuse holder |  |  | TH |  | https://www.digikey.com/product-detail/en/keystone-electronics/3568/36-3568-ND/2137306
1 | F1 | fuse | 3A |  |  | https://www.digikey.com/short/zzbj7z | https://www.digikey.com/product-detail/en/littelfuse-inc/0297003.WXNV/F987-ND/146575
1 | LED1 | LED | green |  | TH, 5mm | https://www.digikey.com/short/zzbjb4 | https://www.digikey.com/product-detail/en/lite-on-inc/LTL2R3KG/160-1684-ND/573574
1 | LED2 | LED | red |  | TH, 5mm | https://www.digikey.com/short/zzbjb5 | https://www.digikey.com/product-detail/en/kingbright/WP7113SRD-E/754-1276-ND/1747675
2 | F2, F3 | fuse, PTC |  |  |  |  | https://www.digikey.com/product-detail/en/littelfuse-inc/RHEF070/RHEF070HF-ND/5029792
2 | OK1, OK2 | optocoupler | 817 |  | TH, DIP | https://www.digikey.com/short/zzbj33 | https://www.digikey.com/product-detail/en/taiwan-semiconductor-corporation/TPC817A-C9G/TPC817AC9G-ND/7359668
2 | Q1, Q2 | MOSFET | N-chan | 1A, 20V | TO-220 | https://www.digikey.com/short/zzbjq4 | https://www.digikey.com/product-detail/en/infineon-technologies/IRL520NPBF/IRL520NPBF-ND/811770
1 | R1 | resistor | 470Ω | 500mW | TH | https://www.digikey.com/short/zzbjjh | https://www.digikey.com/product-detail/en/yageo/FMP100JR-52-470R/470WCT-ND/2058926
7 | TVS | diode, TVS | 16V |  | DO-15 |  | https://www.digikey.com/product-detail/en/P4KE16CA-B/P4KE16CA-B-ND/2501797/
1 | SG1 | buzzer | 3V |  | TH |  | https://www.digikey.com/product-detail/en/pui-audio-inc/AI-3035-TWT-3V-R/668-1204-ND/1745457
1 | X1 | power jack |  |  | TH |  | https://www.digikey.com/product-detail/en/cui-devices/PJ-002AH/CP-002AH-ND/408446
8 | R7, R8, R10, R11, R12, R13, R14, R15 | resistor | 620Ω | 0.25W | TH | https://www.digikey.com/short/zzbjht | https://www.digikey.com/product-detail/en/yageo/CFR-25JB-52-620R/620QBK-ND/2682
2 | R4, R5 | resistor | 4.7kΩ | 0.25W | TH | https://www.digikey.com/short/zzbjhq | https://www.digikey.com/product-detail/en/stackpole-electronics-inc/CF14JT4K70/CF14JT4K70CT-ND/1830366
3 | R2, R6, R9 | resistor | 10kΩ | 0.25W | TH | https://www.digikey.com/short/zzbjhj | https://www.digikey.com/product-detail/en/stackpole-electronics-inc/CF14JT10K0/CF14JT10K0CT-ND/1830374
1 | X2 | connector | JST-PH, 4 pin |  | TH |  | https://www.digikey.com/product-detail/en/B4B-PH-K-S(LF)(SN)/455-1706-ND/926613/
2 | BAT1 | battery clip |  |  | TH |  | https://www.digikey.com/product-detail/en/keystone-electronics/92/36-92-ND/82326
2 | U1 | Arduino Nano headers |  |  | TH | https://www.digikey.com/short/z4p0t3 | https://www.digikey.com/product-detail/en/sullins-connector-solutions/PPTC151LFBN-RC/S7013-ND/810153
1 | X3 | auxiliary header |  |  | TH | https://www.digikey.com/short/z4p0t2
1 | S1 | switch, tactile |  |  | TH | https://www.digikey.com/short/z4pvf1

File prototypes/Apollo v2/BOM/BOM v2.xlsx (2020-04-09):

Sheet: Project Apollo
Category | Name | Price | Match to the project? | Owner | Quantity | Country | Purpose | Notes | URL
Air compressors | 12V 150 PSI Portable Inflator | $8.99 | In evaluation |  | 1 | US |  | Cheap but potentialy noisy | https://www.harborfreight.com/12v-150-psi-portable-inflator-63152.html | I do not think this will work
Air compressor | Requirements: Pressure: 1-1.5 bar, Flow Rate: Minimum 8.4 m3/hour at 1 bar |  |  |  |  |  | To supply required compressed Air | Any decent 110V/230V compressor would work. See JunAir etc. Will need Oil & Water Trap. Comment by EH
Zeolites | 5A Molecular Sieve, five pounds (5 lb) Type 5A 4x8 mesh bead zeolite | $59.99 | In evaluation, ordered | Adi | 5 lb | US |  | need to see which zeolite works best | https://www.ebay.com/itm/5A-Molecular-Sieve-five-pounds-5-lb-Type-5A-4x8-mesh-bead-zeolite/372847613147?ssPageName=STRK%3AMEBIDX%3AIT
Zeolites | 13X Molecular Sieve, five pounds (5 lb) Type 13X 4x8 mesh bead zeolite | $59.99 | In evaluation, ordered | Adi | 5 lb | US | Molecular Sieve | need to see which zeolite works best | https://www.ebay.com/itm/13X-Molecular-Sieve-five-pounds-5-lb-Type-13X-4x8-mesh-bead-zeolite/372847917239?ssPageName=STRK%3AMEBIDX%3AIT
Silica gel beads | "Dry & Dry" (1 Gallon) Premium Silica Gel Blue Indicating(Blue to Pink) Silica Gel Beads Desiccant Beads(Industry Standard 2-4 mm) - Rechargeable(7.5 LBS) | $34.97 | good match |  | 1 gallon | US | ? | blue-to-pink indicator | https://www.amazon.com/Gallon-Premium-Indicating-Industry-Standard/dp/B013L2Z2MY
4-way valve | Tailonz Pneumatic Solenoid Valve 4V210-08 DC12V 1/4 PT Single Coil Pilot-Operated Electric 2 Position 5 Way Connection Type | $13.99 | In evaluation, ordered | Adi | 1 | US | Sequencing Valve | 5-way, 2 positions, 12V | https://www.amazon.com/gp/product/B07SJFV7S3/ref=ppx_yo_dt_b_asin_title_o00_s00?ie=UTF8&psc=1
 | Water Bottle Humidifier (2)
Humidifier |  | $10.95 | good match |  | 2 | US | ? |  | https://www.amazon.com/gp/product/B00KBZFW84/ref=ppx_yo_dt_b_asin_title_o00_s00?ie=UTF8&psc=1
O2 sensors | Hlyjoon Car Front O2 Oxygen Sensor 89465-06240 8946506240 Air Fuel Ratio Lambda Sensor Wiring Harness Lambda Sensor Direct Replacement Part for Toyota Camry 2.0L 2.4L 2.5L | $4.95 | In evaluation | JECS | 1 | US | Testing Purposes | Needs to first test if this sensor works for this application | https://www.amazon.com/Hlyjoon-89465-06240-8946506240-Harness-Replacement/dp/B07WHRCM23
Humidity sensors | HiLetgo 3pcs LM393 Rain Drops Sensor Weather Moisture Monitor Sensor Humidity Sensitivity Module Nickeled Plate 3.3-5V for Arduino | $4.49 | good match |  | 2 | US |  |  | https://www.amazon.com/HiLetgo-Moisture-Humidity-Sensitivity-Nickeled/dp/B01DK29K28
Controller board | ELEGOO UNO R3 Board ATmega328P ATMEGA16U2 with USB Cable Compatible with Arduino IDE Projects, RoHS Compliant | $11.98 | In evaluation | JECS | 1 | US |  | Need to validate if sufficient for this scenario | https://www.amazon.com/ELEGOO-Board-ATmega328P-ATMEGA16U2-Compliant/dp/B01EWOE0UU/
Check valves | 4 Packs Check Valve, 1/4 Inch 6mm PVDF Wear-Resistant One-Way Check Valve | $12.99 |  | Mudder | 1 | US |  | 1/4 inch tubbing | it has 4 items | https://www.amazon.com/-/es/paquetes-retenci%C3%B3n-pulgadas-resistente-combustible/dp/B07X2NZVLH?language=en_US
 | 10pcs Air Pump Check Valves Pipe Fitting for Aquarium Fish Tank | $5.99 |  | RuiLing (https://www.amazon.com/gp/help/seller/at-a-glance.html?seller=A2X3Z6O5H4J9GM&isAmazonFulfilled=1) | 1 | US |  | 0.157inch-4mm tubbing | it has 10 valves | https://www.amazon.com/dp/B07TT68TXG?language=en_US
 | 8mm 5/16" Fuel Non Return One Way Check Valve Petrol Diesel | 8.80% |  | DYWISHKEY | 2 | US |  | 5/16inch-8mm tubbing | https://www.amazon.com/Return-Check-Petrol-Diesel-Aluminium/dp/B06XK215S7
Connectors | (various barb connectors) | < $1 |  | Ken Fujimoto |  | US |  |  | https://www.usplastic.com/search/?it=item&keyword=1%2F4%20npt%20hose%20barb
Tool: NPT tapping | Century Drill & Tool 93202 1/4-18 NPT Tap and 7/16" Drill Combo Pack | $13.98 |  | Ken Fujimoto | 1 | US | Tapping tanks |  | https://www.amazon.com/Century-Drill-Tool-93202-Combo/dp/B0797J88MN?s=hi
Tubing kit | Tailonz Pneumatic 6mm OD 4mm ID Polyurethane PU Air Hose Pipe Tube Kit 10 Meter 32.8ft | $13.99 |  | Ken Fujimoto | 1 | US |  |  | https://www.amazon.com/dp/B07RJ1BYKV/ref=emc_b_5_t
 |  | $257.34
1 Apr 2020 Dan G. added these after discussion with Adi, please vet
Alternate source to above from ebay:
Silica Gel Beads | "Dry & Dry" (1 Gallon) Premium Silica Gel Blue Indicating(Blue to Pink) Silica Gel Beads Desiccant Beads(Industry Standard 2-4 mm) - Rechargeable(7.5 LBS) |  |  |  |  |  |  |  | https://www.ebay.com/itm/1-Gallon-7-5-LBS-Dry-Dry-Premium-Blue-Indicating-Silica-Gel-Desiccant-Beads/271872536108?ssPageName=STRK%3AMEBIDX%3AIT
Check valves | 1/4" fittings |  |  |  |  |  |  |  | https://www.ebay.com/itm/5-Five-1-4-Polypropylene-Standard-Check-Valve-with-Viton-Diaphragm/264328313354?ssPageName=STRK%3AMEBIDX%3AIT
 | 1/8" fittings |  |  |  |  |  |  |  | https://www.ebay.com/itm/5-Five-1-4-Polypropylene-Standard-Check-Valve-with-Viton-Diaphragm/264328313354?ssPageName=STRK%3AMEBIDX%3AIT
Filters | Filters/Exhaust Mufflers 1/4" NPT |  |  |  |  |  |  |  | https://www.ebay.com/itm/4PCS-Pneumatic-Muffler-Filter-Sintered-Bronze-1-8-NPT-Brass-Silencer-M44/113413509269?ssPageName=STRK%3AMEBIDX%3AIT
Tubing | Pneumatic 4mmx6mm tubing, 10m |  |  |  |  |  |  |  | https://www.ebay.com/itm/O-D-4mm-6mm-8mm-PU-Air-Pneumatic-Pipe-Tube-Hose-Air-CLEAR-BLUE-ORANGE/153431107400?ssPageName=STRK%3AMEBIDX%3AIT&var=453476370040
Alternate source for valves and plumbing parts from manufacturer MettleAir - order direct at mettleair.com Shipping within 1-2 days
NOTE: They have 3 classes of parts: for example:
 | MTC6-N02 Basic = plastic connector, nickel-plated brass body, NBR seals ($1)
 | BMTC6-N02 better = nickel-plated body & connector, NBR seals ($2)
 | SMTC6-N02 Best = stainless steel body, Viton seals ($11)
(check where we need all these and exact count later)
Bulkhead connector | Push to Connect Female 1/8" NPT to 6mm OD #MTMF6-N01 | 1.83
Bulkhead connector | Push to Connect Female 1/4" NPT to 6mm OD #MTMF6-N02 | 2.31
5 Way valve | 5 Ports 4 Way 2 Position Valve 1/4" NPT (Exh. 1/8") Wire Leads Single Solenoid DC 12V #4V210-08-DC12W | 24.38
2 Way Valve | 2 Way Valve 1/4" NPT Wire Leads DC 12V Item #2V025-08-DC12W | 15.63
Interchange | 1/4" body x 1/4 NPT Female industrial interchange nipple (this connects to standard compressor hose ) | 2.56
PTC to 1/4 NPT male | Push to Connect to 1/4" NPT male #MTC6-N02 (prepend B for brass) | 0.86
PTC to 1/4 female | Push to Connect to 1/4" NPT female #MTCF6-N02 (prepend B for brass) | 1.34
Other Parts
O-Rings | For the bulkhead fittings from MettleAir. Looks like they are not included: maybe #112 0.50" ID x 11/16 OD
Parts from Harbor Freight (harborfreight.com)
Hose Clamps | Key-type hose clamp assortment 26 pc SKU 67669
Oil/Water separator | may need this or the next one, need to research SKU 68246 | 5.99
Mini Air Line Filter | 1/4 NPT air filter, water separator SKI 68225 | 6.79
Pressure Gauge | 160 PSI 1/4 NPT gauge SKU 64104
Air Hose | if needed to connect to compressor - SKU 62889
Quick Coupler | Use with above air hose - SKU 68241
Regulator Kit w/gauge | 150 PSI air regulator SKU 68223
These are for creating orifices, sizes are TBD, so one option is plugs that can be drilled out.
Plug | 1/8 NPT with hex drive, McMaster 50785K112
Plug | 1/4 NPT with hex drive, McMaster 50785K113
Optional Medical Equipment
Pulse Oximeter | Check patient O2 level (not part of oxygen concentrator specifically) |  |  |  |  |  |  |  | https://www.ebay.com/itm/US-FingerTip-pulse-oximeter-OLED-heart-rate-blood-oxygen-meter-O2-sensor-monitor/271951863525?ssPageName=STRK%3AMEBIDX%3AIT
Output Humidifier | Humidifier and Water bottle (note these can be found at for $2 in Q12 on ebay) | 8.5 |  |  | 1 |  |  |  | https://www.ebay.com/itm/Humidifier-Water-Bottle-and-Tubing-Connector-Elbow-12-for-Oxygen-Concentrator/143519826876?ssPageName=STRK%3AMEBIDX%3AIT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

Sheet: Apollo - prototype v2 (US store
This is the approximate list of materials that were used to build the initial Prototype V2
- Note 1: when exact materials not found, reasonable substitutes were added
- Note 2: Pricing not optimized. Could be a lot lower. Feel free to search cheaper substitiutes!
- Note 3: some minimal amount of bulk order optimization is assumed to start with. Examples: silica beads were acquired in 2x quantity and used in two O2 concentrators.
- Note 4: Not included: tax, shipping (although most items have free shipping included), test instruments, tools, air compressor
- Constraint: fast shipping + building time (we assume DIY building scenario with some urgency)
- Constraint: United States stores only (other countries may have a similar BOM with other local sources)
Category | Name | Price per bulk | Bulk/pack count | Price per item | Quantity needed | Total price | Alternative price | Country | Purpose | O2 compatibility | Notes | Alternatives? | Stores | URL1 | URL2 | URL3
Structure | 5 Gal. Homer Bucket (or equivalent) |  |  | $3.48 | 2 | $6.96 |  | United States | Main structure | Not needed | One bucket inside another. 3"/10 cm clearance between the two | Most large plastic buckets will do | hardware stores | https://www.homedepot.com/p/The-Home-Depot-5-Gal-Homer-Bucket-05GLHD2/100087613
 | 5-gal. Homer Leakproof Lid |  |  | $1.76 | 1 | $1.76 |  | United States | Lid, supporting electronics, fan | Not needed |  | Any lid matching bucket will do | hardware stores | https://www.homedepot.com/p/The-Home-Depot-5-gal-Homer-Leakproof-Lid-5GLD-ORANGE-LID-for-5GL-HOMER-PAIL/202264044
 | 1ft x 1 ft Acrylic or Polycarbonate transparent plate |  |  | $0.50 | 1 | $0.50 |  | United States | Supporting the upper part of the pneumatics | Not needed | Should be a few mmk thick. Can be acquired as scrap plastics ($2/lb?) |  | Tap Plastics
 | 2 liter soda bottle |  |  | $0.49 | 4 | $1.96 |  | United States | Zeolite/silica tanks, O2 storage tank | Not needed | Prices vary. | Any PET soda bottle will work | Retail stores (Fred Meyer, Safeway, etc) | https://www.fredmeyer.com/p/kroger-club-soda/0001111049345
Fittings | Bronze Exhaust Muffler,Pneumatic Muffler Sintered Bronze Exhaust Muffler 1/8" NPT Brass Body (Pack of 10) | $8.99 | 10 | $0.90 | 7 | $6.29 |  | United States | Filter to prevent beads from entering into the piping | Yes | There is also a 1/4 NPT variant | Alternative: aquarium air stone? (not sure if O2 compatible) | Amazon Prime | https://www.amazon.com/gp/product/B07L8HKLSH/ref=ppx_yo_dt_b_asin_title_o00_s00?ie=UTF8&psc=1
 | PTC Straight Bulkhead Female Fitting 1/4" OD, 1/8" NPT | $55.35 | 10 | $5.54 | 7 | $38.74 |  | United States | Adapter from brass filter to PTC connector | Yes |  | See "fittings" doc for alternatives | Amazon Prime | https://www.amazon.com/gp/product/B00S51ESSG/ref=ppx_yo_dt_b_asin_title_o01_s00?ie=UTF8&psc=1
 | (alternative to above) EDGE INDUSTRIAL Brass REDUCING HEX Bushing 1/4" Male NPT X 1/8" Female NPT Fuel / AIR/ Water / Oil/ Gas WOG (Qty 010) | $19.95 | 10 | $2.00 | 7 |  | $13.96 | United States | A different adapter variant to PTC Straight Bulkhead Female Fitting | Yes | Needs separate PTC adapter (see below) |  | Amazon Prime | https://www.amazon.com/gp/product/B07WSR6GZB/ref=ppx_yo_dt_b_asin_title_o00_s00?ie=UTF8&psc=1
 | (alternative to above) Push to Connect Tube Fitting, Adapter, 1/4" Tube OD x 1/4" NPT Female Straight Push Fit Fittings 5 Packs | $10.99 | 5 | $2.20 | 7 |  | $15.39 | United States | together with above | <TBD> |  |  | Amazon Prime | https://www.amazon.com/gp/product/B07D2C2G9W/ref=ppx_yo_dt_b_asin_title_o01_s00?ie=UTF8&psc=1
 | 10Pcs 1/4" PT Male Thread 6mm Straight Pneumatic Push in Quick Fitting Connectors for PETF Tube | $6.99 | 10 | $0.70 | 4 |  | $2.80 | United States | Two needed for 2-way valve, 2 for air filter | <TBD> | More might be needed whether the 5-way valve comes with PTC included | (many) | Amazon Prime | https://www.amazon.com/gp/product/B07124KF69/ref=ppx_yo_dt_b_asin_title_o07_s00?ie=UTF8&psc=1
 | Tailonz Pneumatic 1/4 Inch od Push to Connect Fittings Pneumatic Fittings Kit 10 Spliters+10 Elbows+10 tee+10 Straight (40 pcs) |  |  | $14.99 | 1 | $14.99 |  | United States | TBD(Adi) - detail which fittings we need | <TBD> | Only some fittings needed. Research TBD. Could be a lot cheaper in bulk | (many) | Amazon Prime | https://www.amazon.com/gp/product/B07RSLDDBR/ref=ppx_yo_dt_b_asin_title_o02_s01?ie=UTF8&psc=1
 | Tailonz Pneumatic 1/4 Inch OD 10 Meters PU Air Tubing Pipe Hose Pu Air Hose for Air Line Tubing or Fluid Transfer Tubing | $11.99 | 10 | $1.20 | 2 | $2.40 |  | United States | O2/air transport | <TBD> | Need about 2 meters of blue air hose |  | Amazon Prime | https://www.amazon.com/Tailonz-Pneumatic-Meters-Tubing-Transfer/dp/B07R2F97T9/
 | Lemoy 1/4" OD Quick Connect Push In to Connect Water Tube Fitting for RO Reverse Osmosis Water Filter Fittings Pack of 30 |  |  | $11.99 | 1 |  | $11.99 | United States | Various fittings | <TBD> | Only some fittings needed. Research TBD. Could be a lot cheaper in bulk |  | Amazon Prime | https://www.amazon.com/gp/product/B07H2TR3LQ/ref=ppx_yo_dt_b_asin_title_o07_s01?ie=UTF8&psc=1
O-ring seals | Performance Tool W5239 Brown 180pc Polymer Viton O-Ring Assortment, 18 Sizes 180 Pieces | $21.99 | 180 | $0.12 | 7 | $0.86 |  | United States | Bottle/tank fitting seal | Yes | Need to find exact sources | <TBD> | Amazon, TBD | https://www.amazon.com/Performance-Tool-W5239-Polymer-Assortment/dp/B01N8ZLHQO/
Check valves | Lemoy 1/4" Tube Push Fit Straight Quick Connect Check Valve for RO Water Reverse Osmosis System (Pack of 5) (5 pack+2 ball valve) | $9.99 | 5 | $2.00 | 2 | $4.00 |  | United States | Check valves | <TBD> | Research TBD. Could be a lot cheaper in bulk | TBD | Amazon Prime | https://www.amazon.com/gp/product/B0743863HN/ref=ppx_yo_dt_b_asin_title_o02_s01?ie=UTF8&psc=1
5-way valve | Tailonz Pneumatic Solenoid Valve 4V210-08 DC12V 1/4 PT Single Coil Pilot-Operated Electric 2 Position 5 Way Connection Type |  |  | $13.99 | 1 | $13.99 |  | United States | 5-way valve | <TBD> | TODO: Need O2-compatible seals! | Many alternatives | Amazon | https://www.amazon.com/gp/product/B07SJFV7S3/ref=ppx_yo_dt_b_asin_title_o08_s01?ie=UTF8&psc=1 | https://www.amazon.com/gp/product/B01J3CE3EE/ref=ppx_yo_dt_b_asin_title_o04_s01?ie=UTF8&psc=1 | https://www.amazon.com/gp/product/B00EQ1X1U0/ref=ppx_yo_dt_b_asin_title_o04_s02?ie=UTF8&psc=1
2-way valve | 1/4inch DC 12V 2 Way Normally Closed Electric Solenoid Air Valve |  |  | $9.95 | 1 | $9.95 |  | United States | 2-way valve | <TBD> | TODO: Need O2-compatible seals! | Many alternatives | Amazon | https://www.amazon.com/gp/product/B074Z5SDG3/ref=ppx_yo_dt_b_asin_title_o08_s00?ie=UTF8&psc=1
Copper tubing | 1/4 in. O.D. x 10 ft. Soft Copper Refrigeration Coil Tubing |  |  | $9.71 | 1 | $9.71 |  | United States | copper tubing for cooling compressed air | Not needed | could be cheaper somewhere else? |  | Home Depot | https://www.homedepot.com/p/Everbilt-1-4-in-O-D-x-10-ft-Soft-Copper-Refrigeration-Coil-Tubing-1-4-R-10RE/203654086
Compressed air female coupler | 1/4 In. Female Steel Automotive Coupler |  |  | $3.49 | 1 | $3.49 |  | United States | Compressed air female coupler |  | could be cheaper somewhere else? | Male coupler is cheaper | Harbor Freight Tools | https://www.harborfreight.com/air-tools-compressors/air-compressor-accessories/14-in-female-steel-automotive-coupler-63552.html
Air filter | Mini Air Line filter (Harbor Freight) |  |  | $6.79 | 1 | $6.79 |  | United States | air filter + water separator | Not needed | could be cheaper somewhere else? | needs to be drained periodically | Harbor Freight Tools | https://www.harborfreight.com/mini-air-line-filter-68225.html
 | Mini Air Filter 1/4 in. NPT (MP513803AV) - Home Depot |  |  | $12.98 | 1 |  | $12.98 | United States | air filter + water separator | Not needed | could be cheaper somewhere else? | Allows continuous water drain | Home Depot | https://www.homedepot.com/p/Campbell-Hausfeld-Mini-Air-Filter-1-4-in-NPT-MP513803AV-MP513803AV/301197429
 |  |  |  |  |  |  |  | United States
Microcontroller board | Arduino Uno |  |  | $23.86 | 1 |  | $23.86 | United States | main microcontroller board | Not needed | Arduino Uno-compatible | Many alternatives for a few $ | Amazon | https://www.amazon.com/Arduino-A000066-ARDUINO-UNO-R3/dp/B008GRTSV6
 | ELEGOO UNO R3 Board ATmega328P ATMEGA16U2 with USB Cable Compatible with Arduino IDE Projects, RoHS Compliant |  |  | $13.98 | 1 |  | $13.98 | United States | main microcontroller board | Not needed | Arduino Uno-compatible | Many alternatives for a few $ | Amazon, ebay, etc | https://www.amazon.com/ELEGOO-Board-ATmega328P-ATMEGA16U2-Compliant/dp/B01EWOE0UU
 | UNO R3 ATmega328P CH340G Development Board Pin For Arduino With USB Cable |  |  | $3.49 | 1 | $3.49 |  | online | main microcontroller board | Not needed | Arduino Uno-compatible | Many alternatives for a few $ | ebay | https://www.ebay.com/itm/UNO-R3-ATmega328P-CH340G-Development-Board-Pin-For-Arduino-With-USB-Cable/254454313876?epid=4026019589
Valve driver board | High-Power ULN2003 Stepper Motor Driver Board Test Module for Arduino AVR SMD |  |  |  | 1 | $1.94 |  |  |  |  |  | Many alternatives for a few $ | Amazon, ebay, etc | https://www.amazon.com/High-Power-ULN2003-Stepper-Driver-Arduino/dp/B07SMXSKTG
Silica beads | Dry & Dry" (1 Gallon Premium Silica Gel Blue Indicating(Blue to Pink) Silica Gel Beads Desiccant Beads(Industry Standard 2-4 mm) - Rechargeable(7.5 LBS) Moisture Absorber Silica Gel | $36.96 | 1 gallon |  | 0.5 gallon | $18.48 |  | United States | Drying silica bed | Not needed | Could be a lot cheaper in bulk (TBD) | Could be recycled? | Amazon, ebay, etc | https://www.amazon.com/gp/product/B013L2Z2MY/ref=ppx_yo_dt_b_asin_title_o05_s00?ie=UTF8&psc=1
13X zeolite | 13X Molecular Sieve, five pounds (5 lb) Type 13X 4x8 mesh bead zeolite |  |  | $59.99 | 5 lb bag | $59.99 |  | United States | Zeolite bed | Yes | Could be a lot cheaper in bulk
Cooling fan | 120mm 4Pins 12V PC CPU Host Chassis Computer Case IDE Fan Cooling Cooler BLACK |  |  | $4.99 | 1 | $4.99 |  | <ebay> | Cooling the copper loop | Not needed |  | Many alternatives for a few $ | Amazon, ebay, etc | https://www.ebay.com/itm/120mm-4Pins-12V-PC-CPU-Host-Chassis-Computer-Case-IDE-Fan-Cooling-Cooler-BLACK/183914292085
Power supply | TMEZON 12 Volt 2A Power Adapter Supply AC to DC 2.1mm X 5.5mm Plug 12v 2 Amp Power Supply Wall Plug Extra Long 8 Foot Cord |  |  | $7.99 | 1 |  | $7.99 | internet | Power for microcontroller, valves | Not needed |  | Many alternatives for a few $ | Amazon, ebay, etc | https://www.amazon.com/TMEZON-Power-Adapter-Supply-2-1mm/dp/B00Q2E5IXW/
 | AC DC 12V 2A 110-240V POWER SUPPLY ADAPTER CHARGER FOR 3528/5050 LED PLUG FBDU |  |  |  | 1 | $2.89 |  |  | Power for microcontroller, valves | Not needed |  |  |  | https://www.ebay.com/itm/AC-DC-12V-2A-110-240V-POWER-SUPPLY-ADAPTER-CHARGER-FOR-3528-5050-LED-PLUG-FBDU/153298282224
O2 Flowmeter | LZQ-3 height 90MM flowmeter 0-5 LPM flow meter for Oxygen /air/gas |  |  |  | 1 | $7.37 |  | internet | O2 flow meter | Yes |  | Many alternatives for a few $ | ebay? | https://www.ebay.com/itm/LZQ-3-height-90MM-flowmeter-0-5-LPM-flow-meter-for-Oxygen-air-gas/331264642634
M3 screws assortment | 90pcs M3 Stainless Steel Hex Socket Head Cap Screw Assortment Kit #M1957 QL |  |  |  | 1 | $5.28 |  | internet |  | Not needed |  |  | ebay? | https://www.ebay.com/itm/90pcs-M3-Stainless-Steel-Hex-Socket-Head-Cap-Screw-Assortment-Kit-M1957-QL/181947698614
TOTAL |  |  |  |  |  | $226.82

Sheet: Testingdevelopment
Category | Name | Price per bulk | Bulk/pack count | Price per item | Quantity needed | Total price | Country | Purpose | O2 compatibility | Notes | Alternatives? | Stores | URL1 | URL2 | URL3
Needle valves | Litorange 2 Pack Heavy Duty Brass Replacement Control Needle Valve 1/4" Female NPT X 1/4" Female NPT Connection | $14.99 | 2 | $7.50 | 2 | $14.99 | United States | Fine-tune orifice size after zeolite tanks | Yes | Much cheaper valve in final product | orifice in cap | Amazon Prime | https://www.amazon.com/gp/product/B07YFR72JP/ref=ppx_yo_dt_b_asin_title_o03_s00?ie=UTF8&psc=1 | https://www.amazon.com/gp/product/B00FBQ2D62/ref=ppx_yo_dt_b_asin_title_o02_s00?ie=UTF8&psc=1
Pressure gauge | PIC Gauge 102D-158D-10/32 1.5" Dial, 0/60 psi Range, 1/8" Male NPT Connection Size, Center Back Mount Dry Pressure Gauge with a Black Steel Case, Brass Internals, Chrome Bezel, Plastic Lens, and 10/32 Internal Tap |  |  | $4.11 | 2 | $8.22 | United States | Monitor prototype | Not known | Could be useful to diagnose leaks | digital sensors | Amazon Prime | https://www.amazon.com/gp/product/B00FBJJBZU/ref=ppx_yo_dt_b_asin_title_o02_s00?ie=UTF8&psc=1

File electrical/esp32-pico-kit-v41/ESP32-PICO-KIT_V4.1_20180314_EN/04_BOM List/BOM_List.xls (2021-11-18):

ESP32-PICO-KIT_V4.1 BOM_List(V0.9)
ID | Qty | Ref Des | Value | Package | ICs | Description
1 | 1 | ANT1 | Proant440 | PROANTONBOARD440 | Antenna | 3D Antenna
2 | 2 | C2,C4 | 10uF/25V(10%) | 0603C | Capacitance | Ceramic Capacitor
3 | 5 | C6,C7,C12,C16,C19 | 0.1uF/25V(10%) | 0402C | Capacitance | Ceramic Capacitor
4 | 1 | C15 | 10uF/6.3V(10%) | 0402C | Capacitance | Ceramic Capacitor
5 | 1 | C17 | 2.7pF±0.5pF/25V | 0402C | Capacitor | Ceramic Capacitor
6 | 1 | C18 | 1.6nH±0.3nH | 0402C | Inductor | Inductor
7 | 1 | D1 | RED LED | 0603D/A | LED | Red LED
8 | 1 | D2 | BAT760-7 | SOD-323 | Diode | Diode
9 | 3 | D3,D4,D5 | LESD5D5.0CT1G | SOD-523 | ESD | ESD 5V
10 | 1 | J1 | USB_CON8 | USB_5P | Connector | USB Connector
11 | 2 | J2,J3 | 2.54mm single-row pin headers 17P | CON20_2P54 | Connector | Male Header
12 | 1 | L1 | 4.7pF±0.5pF/25V | 0402C | Capacitor | Ceramic Capacitor
13 | 2 | Q1,Q2 | S8050(NPN) | SOT-23-3 | Transistor | Transistor(NPN)
14 | 2 | R1,R27 | 2K(1%) | 0402R | Resistor | Resistor
15 | 5 | R3,R4,R6,R7,R21 | 0R(1%) | 0402R | Resistor | Resistor
16 | 2 | R15,R16 | 1K(1%) | 0402R | Resistor | Resistor
17 | 3 | R19,R20,R22 | 10K(1%) | 0402R | Resistor | Resistor
18 | 1 | R24 | 22.1K(1%) | 0402R | Resistor | Resistor
19 | 1 | R26 | 47.5K(1%) | 0402R | Resistor | Resistor
20 | 2 | SW1,SW2 | SW PUSHBUTTON | SW_3X4X2MM | Push Button | Push Button
21 | 1 | U1 | AMS1117-3.3 | SOT-223 | Power IC | Power IC
22 | 1 | U4 | CP2102N | QFN28-5X5-0P5 | IC Chip | USB2UART Bridge
23 | 1 | U5 | ESP32-PICO-D4 | QFN48_7X7 | IC Chip | ESP32-SIP

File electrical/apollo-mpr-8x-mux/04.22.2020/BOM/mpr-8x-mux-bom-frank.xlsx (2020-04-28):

Qty | Designator | Footprint | Comment | LCSC Part # | Description (optional)
2 | C1, C2 | C0805 | 100n | C49678 | Capacitor
2 | C3, C4 | C1206 | 10u | C127946 | Capacitor Polarized
1 | LED1 | CHIP_LED0603 | LED | C205443 | LED
1 | U1 | TSSOP-24 | TCA9548A | C130026 | TCA9548A I2C Multiplexer
1 | R4 | R0805 | 1K | C17513 | Resistor
10 | Q1, Q2, Q3, Q4, Q5, Q6, Q7, Q8, Q9, Q10 | SOT-23-3 | 2N7002 | C12779
1 | D2 | SOD-323 | 3V6 | C12453 | Zener Diode
1 | R13 | R0805 | 470R | C17710 | Resistor
11 | R1, R2, R3, R5, R6, R7, R8, R9, R10, R11, R12 | R0805 | 4K7 | C17673 | Resistor
1 | IC1 | SOT-223 | LM1117-3V3 | C347222 | Voltage Regulator LM1117
1 | D1 | SOD-323 | SCHOTTKY | C64886 | Schottky Diode

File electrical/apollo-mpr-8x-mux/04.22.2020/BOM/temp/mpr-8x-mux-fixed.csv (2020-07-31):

Qty | Comment | Footprint | Designator | Description | MF | MPN | OC_FARNELL | OC_NEWARK | Value | Device
2 | 100n | 0805_C | C1, C2 | Capacitor |  |  |  |  |  | CAP0805
2 | 10u | 1206_C | C3, C4 | Capacitor Polarized |  |  |  |  |  | CAP_POL1206-KIT
1 |  | 0603 | LED1 | LEDs |  |  |  |  |  | LED0603
1 |  | TSSOP24 | U1 | TCA9548A I2C Multiplexer |  |  |  |  |  | TCA9548A
1 | 1K | 0805 | R4 | Resistor |  |  |  |  | 1K | RESISTOR0805-RES
10 | 2N7002D | SOT23-3 | Q1, Q2, Q3, Q4, Q5, Q6, Q7, Q8, Q9, Q10 |  |  |  |  |  | 2N7002D | MOSFET-NCHANNELSMD
1 | 3V6 | SOD-323 | D2 | Zener Diode |  |  |  |  | 3V6 | DIODE-ZENERSOD
1 | 470R | 805 | R13 | Resistor |  |  |  |  | 470R | RESISTOR0805-RES
11 | 4K7 | 805 | R1, R2, R3, R5, R6, R7, R8, R9, R10, R11, R12 | Resistor |  |  |  |  | 4K7 | RESISTOR0805-RES
1 | LM1117-3V3 | SOT223 | IC1 | Voltage Regulator LM1117 |  |  |  |  | LM1117-3V3 | V_REG_LM1117SOT223
1 | MCP23017SS | SSOP28 | U2 | http://ww1.microchip.com/downloads/en/DeviceDoc/21952a.pdf | MICROCHIP | MCP23017-E/SS | 1467674 | 31K2960 | MCP23017SS | MCP23017SS
1 | SCHOTTKY | SOD-323 | D1 |  |  |  |  |  | SCHOTTKY | DIODE-SCHOTTKYSOD

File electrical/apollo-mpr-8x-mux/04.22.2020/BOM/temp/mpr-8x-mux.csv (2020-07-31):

Qty | Value | Device | Package | Parts | Description | MF | MPN | OC_FARNELL | OC_NEWARK
2 |  | CAP0805 | 0805 | C1, C2 | Capacitor
2 |  | CAP_POL1206-KIT | EIA3216-KIT | C3, C4 | Capacitor Polarized
1 |  | LED0603 | LED-0603 | LED1 | LEDs
1 |  | M081X08 | 1X08 | JP1 | Header 8
1 |  | TCA9548A | TSSOP24 | U1 | TCA9548A I2C Multiplexer
1 | 1K | RESISTOR0805-RES | 0805 | R4 | Resistor
10 | 2N7002D | MOSFET-NCHANNELSMD | SOT23-3 | Q1, Q2, Q3, Q4, Q5, Q6, Q7, Q8, Q9, Q10
1 | 3V6 | DIODE-ZENERSOD | SOD-323 | D2 | Zener Diode
1 | 470R | RESISTOR0805-RES | 0805 | R13 | Resistor
11 | 4K7 | RESISTOR0805-RES | 0805 | R1, R2, R3, R5, R6, R7, R8, R9, R10, R11, R12 | Resistor
1 | LM1117-3V3 | V_REG_LM1117SOT223 | SOT223 | IC1 | Voltage Regulator LM1117
1 | MCP23017SS | MCP23017SS | SSOP28 | U2 | http://ww1.microchip.com/downloads/en/DeviceDoc/21952a.pdf | MICROCHIP | MCP23017-E/SS | 1467674 | 31K2960
8 | RJ45-8-2-CONEC-1 | RJ45-8-2-CONEC-1 | CONEC-33TS3004ST-88001 | X1, X2, X3, X4, X5, X6, X7, X8
1 | SCHOTTKY | DIODE-SCHOTTKYSOD | SOD-323 | D1
4 | STAND-OFF | STAND-OFF | STAND-OFF | JP2, JP3, JP4, JP5 | Stand Off
8 | TP-GROUP-X8-2X04 | TP-GROUP-X8-2X04 | 2X4 | X9, X10, X11, X12, X13, X14, X15, X16

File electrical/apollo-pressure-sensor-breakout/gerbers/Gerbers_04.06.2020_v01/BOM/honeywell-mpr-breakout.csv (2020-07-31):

Qty | Value | Device | Package | Parts | Description
1 | 100n | CAP0805 | 0805 | C1 | Capacitor
1 | 1u | CAP0805 | 0805 | C2 | Capacitor
2 | 4K7 | RESISTOR0805-RES | 0805 | R1, R2 | Resistor
1 | FB-0805 | FB-0805 | 0805 | FB1
1 | HONEYWELL-MPR-SMD-GAUGE | HONEYWELL-MPR-SMD-GAUGE | HONEYWELL-MPR-GAUGE | U1
1 | M04X2 | M04X2 | 2X4 | X2
1 | RJ45-8-2-CONEC-1 | RJ45-8-2-CONEC-1 | CONEC-33TS3004ST-88001 | X1
4 | STAND-OFF | STAND-OFF | STAND-OFF | JP1, JP2, JP3, JP4 | Stand Off

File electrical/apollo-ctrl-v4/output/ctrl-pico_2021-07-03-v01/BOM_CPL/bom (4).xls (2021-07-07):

Comment | Designator | Package | LCSC Part
0805W8F5601T5E | R22 | 0805 | C4382
0805W8F1002T5E | R1,R9,R10,R11,R12,R13,R14,R15,R16,R17,R19,R20,R21,R23,R24 | 0805 | C17414
MLT-8540 | SG1 | BUZZER-SMT-4 | C95300
SS34 | D1,D3 | SMA-DIODE | C8678
CL21A106KAYNNNE | C2 | 0805 | C15850
0805W8F2203T5E | R18 | 0805 | C17556
AO3400-SOT23-3L | Q1 | SOT23-3 | C332102
0805W8F1000T5E | R5,R6 | 0805 | C17408
19-217/GHC-YR1S2/3T | D2 | LED-0603 | C72043
OVZ101M1CTR-0606 | C8 | PANASONIC_D | C134878
0805W8F3301T5E | R7,R8 | 0805 | C26010
CL21B105KBFNNNE | C1,C3,C7 | 0805 | C28323

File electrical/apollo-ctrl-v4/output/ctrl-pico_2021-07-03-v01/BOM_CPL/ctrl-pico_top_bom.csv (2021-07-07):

Comment | Designator | Footprint | LCSC Part #
1u | C1 C3 C7 | 0805
3.3K | R7 R8 | 0805
3A | D1 D3 | SMA-DIODE
5.6K | R22 | 0805
10K | R1 R9 R10 R11 R12 R13 R14 R15 R16 R17 R19 R20 R21 R23 R24 | 0805
10u | C2 | 0805
47uF | C8 | PANASONIC_D | C134878
100 | R5 R6 | 0805
220K | R18 | 0805
BACKLIGHT | JP1 | SMT-JUMPER_2_NO_NO-SILK
BUZZER-POL | SG1 | BUZZER-SMT-4
DNP | C4 R2 R3 R4 | 0805
DNP (24LC01) | U1 | SO08
ON | D2 | LED-0603
RESET | JP2 | SMT-JUMPER_2_NC_PASTE_NO-SILK
SOT23-3 | Q1 | SOT23-3

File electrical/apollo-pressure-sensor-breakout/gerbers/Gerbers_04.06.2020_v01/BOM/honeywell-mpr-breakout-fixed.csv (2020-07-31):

Qty | Comment | Footprint | Designator
1 | 100n | 0805_C | C1
1 | 1u | 0805_C | C2
2 | 4K7 | 0805_R | R1, R2
1 | BEADS 0805 ROHS | 0805 | FB1

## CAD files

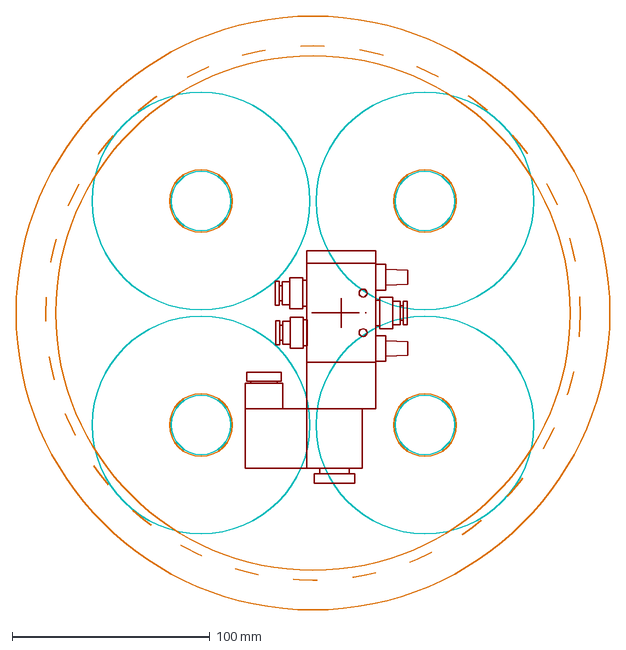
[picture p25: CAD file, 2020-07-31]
prototypes/Apollo v2/Drawings/bottom bucket.dxf
300.0 x 300.0 mm

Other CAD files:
prototypes/Apollo v2/Drawings/top bucket view.dwg
prototypes/Apollo v1/Drawings/apollo01.scad
docs/Faztek_cap v27.f3d
prototypes/Apollo v2/Drawings/bottom bucket.dwg

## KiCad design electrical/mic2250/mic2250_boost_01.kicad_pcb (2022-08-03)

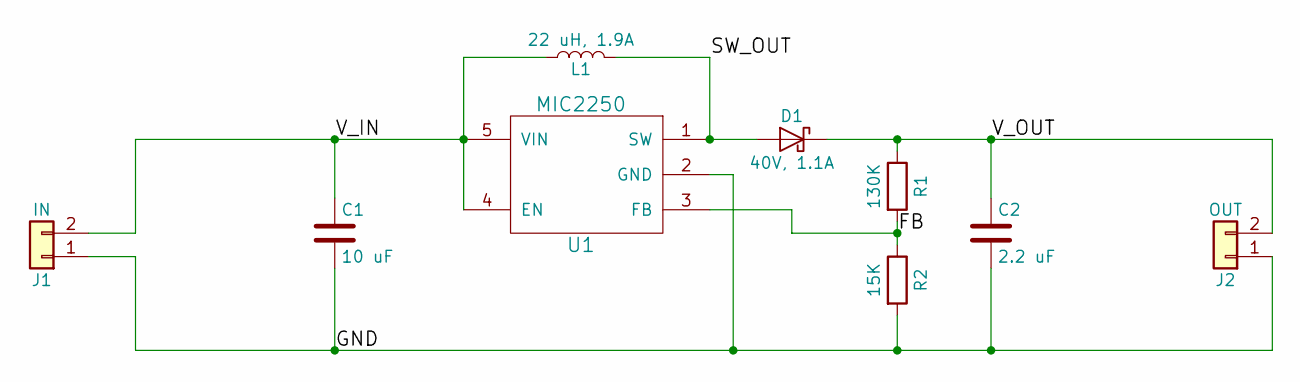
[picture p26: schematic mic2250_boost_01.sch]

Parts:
C1: 10 uF; C_1206
C2: 2.2 uF; C_1206
D1: 40V, 1.1A; do219ab
J1: IN; Pin_Header_Straight_1x02_Pitch2.54mm
J2: OUT; Pin_Header_Straight_1x02_Pitch2.54mm
L1: 22 uH, 1.9A; MURATA-DG6050C
R1: 130K; R_0805
R2: 15K; R_0805
U1: MIC2250; SOT-753_(TSOP-5)_Handsoldering

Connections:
/FB: R1.2, R2.1, U1.3 (FB)
/GND: C1.2, C2.2, J1.1, J2.1, R2.2, U1.2 (GND)
/SW_OUT: D1.2 (A), L1.2, U1.1 (SW)
/V_IN: C1.1, J1.2, L1.1, U1.4 (EN), U1.5 (VIN)
/V_OUT: C2.1, D1.1 (K), J2.2, R1.1

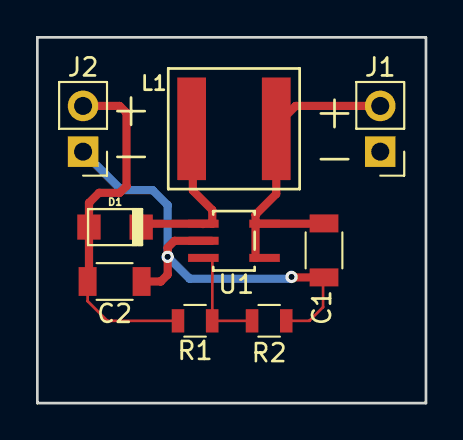
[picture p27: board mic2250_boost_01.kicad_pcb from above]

Board: 2 copper layers, 21.6 x 20.3 mm, 9 parts (0 on the bottom side), 5 nets.

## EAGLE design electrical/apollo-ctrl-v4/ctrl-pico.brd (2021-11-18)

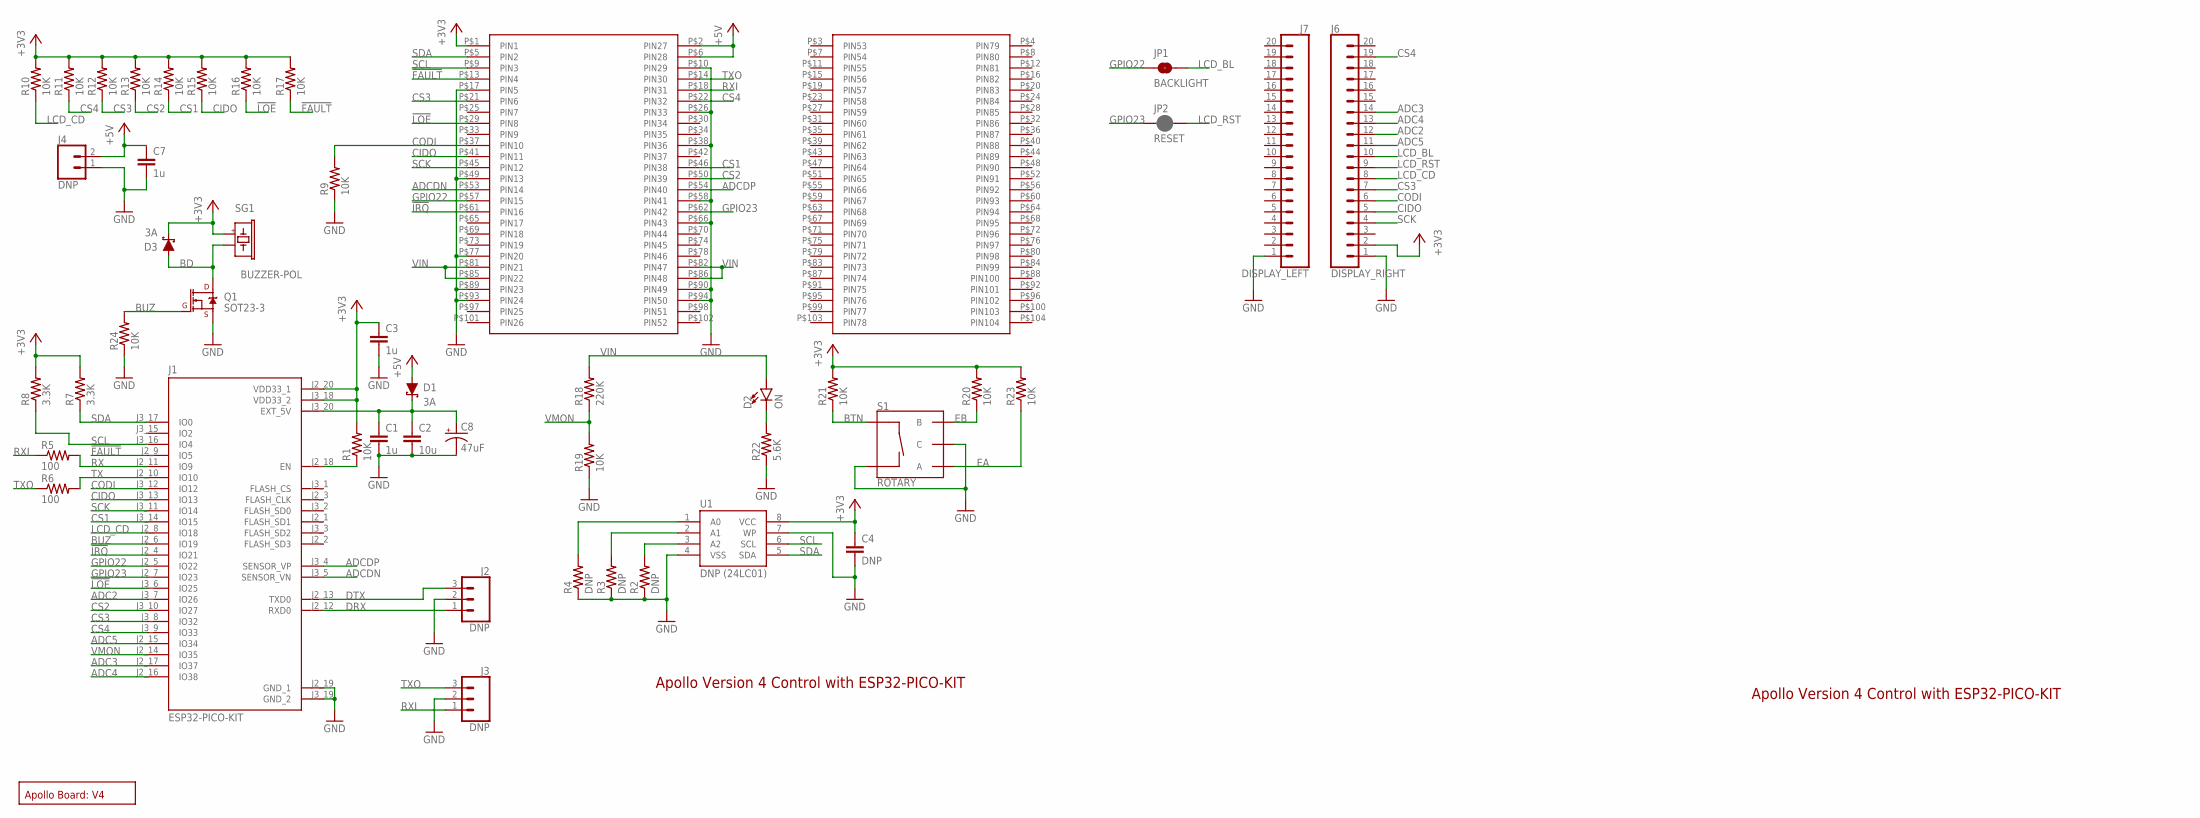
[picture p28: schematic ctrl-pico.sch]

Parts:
C1, C3, C7: 1u; 0805
C2: 10u; 0805
C4: DNP; 0805
C8: 47uF; PANASONIC_D
D1, D3: 3A; SMA-DIODE
D2: ON; LED-0603
J1: ESP32-PICO-KIT; XCVR_ESP32-PICO-KIT
J2, J3: DNP; 1X03
J4: DNP; 1X02
J6: DISPLAY_RIGHT; 1X20
J7: DISPLAY_LEFT; 1X20
JP1: BACKLIGHT; SMT-JUMPER_2_NO_NO-SILK
JP2: RESET; SMT-JUMPER_2_NC_PASTE_NO-SILK
Q1: SOT23-3
R1, R9, R10, R11, R12, R13, R14, R15, R16, R17, R19, R20, R21, R23, R24: 10K; 0805
R2, R3, R4: DNP; 0805
R5, R6: 100; 0805
R7, R8: 3.3K; 0805
R18: 220K; 0805
R22: 5.6K; 0805
S1: ROTARY; ROTARY_ENC_PLAIN
SG1: BUZZER-POL; BUZZER-SMT-4
U1: DNP (24LC01); SO08
U$1: PC104_CONNECTOR
U$2: BOARD_TEMPLATE1; BOARD_TEMPLATE

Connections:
!FAULT!: J1.J2_9 (IO5), R17.1, U$1.P$13 (PIN4)
!IRQ!: J1.J2_4 (IO21), U$1.P$61 (PIN16)
!LOE!: J1.J3_6 (IO25), R16.1, U$1.P$29 (PIN8)
+3V3: C3.1, C4.1, D3.C, J1.J2_20 (VDD33_1), J1.J3_18 (VDD33_2), J6.2, R1.2, R7.2, R8.2, R10.2, R11.2, R12.2, R13.2, R14.2, R15.2, R16.2, R17.2, R20.2, R21.2, R23.2, SG1.BP, U1.8 (VCC), U$1.P$1 (PIN1)
+5V: C7.1, D1.A, J4.2, U$1.P$2 (PIN27), U$1.P$6 (PIN28)
A0: R4.2, U1.1 (A0)
A1: R3.2, U1.2 (A1)
A2: R2.2, U1.3 (A2)
ADC2: J1.J3_7 (IO26), J6.12
ADC3: J1.J2_17 (IO37), J6.14
ADC4: J1.J2_16 (IO38), J6.13
ADC5: J1.J2_15 (IO34), J6.11
ADCDN: J1.J3_5 (SENSOR_VN), U$1.P$53 (PIN14)
ADCDP: J1.J3_4 (SENSOR_VP), U$1.P$54 (PIN40)
BD: D3.A, Q1.3 (D), SG1.BM (N)
BTN: R21.1, S1.SW+
BUZ: J1.J2_6 (IO19), Q1.1 (G), R24.2
CIDO: J1.J3_13 (IO13), J6.5, R15.1, U$1.P$41 (PIN11)
CODI: J1.J3_12 (IO12), J6.6, R9.2, U$1.P$37 (PIN10)
CS1: J1.J3_14 (IO15), R14.1, U$1.P$46 (PIN38)
CS2: J1.J3_10 (IO27), R13.1, U$1.P$50 (PIN39)
CS3: J1.J3_8 (IO32), J6.7, R12.1, U$1.P$21 (PIN6)
CS4: J1.J3_9 (IO33), J6.19, R11.1, U$1.P$22 (PIN32)
DRX: J1.J2_12 (RXD0), J2.1
DTX: J1.J2_13 (TXD0), J2.3
EA: R23.1, S1.A
EB: R20.1, S1.B
EN: J1.J2_18 (EN), R1.1
GND: C1.2, C2.2, C3.2, C4.2, C7.2, C8.-, J1.J2_19 (GND_1), J1.J3_19 (GND_2), J2.2, J3.2, J4.1, J6.1, J7.1, Q1.2 (S), R2.1, R3.1, R4.1, R9.1, R19.1, R22.1, R24.1, S1.C, S1.SW-, U1.4 (VSS), U1.7 (WP), U$1.P$10 (PIN29), U$1.P$17 (PIN5), U$1.P$26 (PIN33), U$1.P$38 (PIN36), U$1.P$49 (PIN13), U$1.P$58 (PIN41), U$1.P$66 (PIN43), U$1.P$77 (PIN20), U$1.P$89 (PIN23), U$1.P$90 (PIN49), U$1.P$93 (PIN24), U$1.P$94 (PIN50)
GPIO22: J1.J2_5 (IO22), JP1.1, U$1.P$57 (PIN15)
GPIO23: J1.J2_7 (IO23), JP2.1, U$1.P$62 (PIN42)
LCD_BL: J6.10, JP1.2
LCD_CD: J1.J2_8 (IO18), J6.8, R10.1
LCD_RST: J6.9, JP2.2
RX: J1.J2_11 (IO9), R5.2
RXI: J3.1, R5.1, U$1.P$18 (PIN31)
SCK: J1.J3_11 (IO14), J6.4, U$1.P$45 (PIN12)
SCL: J1.J3_16 (IO4), R8.1, U1.6 (SCL), U$1.P$9 (PIN3)
SDA: J1.J3_17 (IO0), R7.1, U1.5 (SDA), U$1.P$5 (PIN2)
TX: J1.J2_10 (IO10), R6.2
TXO: J3.3, R6.1, U$1.P$14 (PIN30)
USB5V: C1.1, C2.1, C8.+, D1.C, J1.J3_20 (EXT_5V)
VIN: D2.A, R18.2, U$1.P$81 (PIN21), U$1.P$82 (PIN47), U$1.P$85 (PIN22), U$1.P$86 (PIN48)
VLED: D2.C, R22.2
VMON: J1.J2_14 (IO35), R18.1, R19.2

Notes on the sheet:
Apollo Version 4 Control with ESP32-PICO-KIT

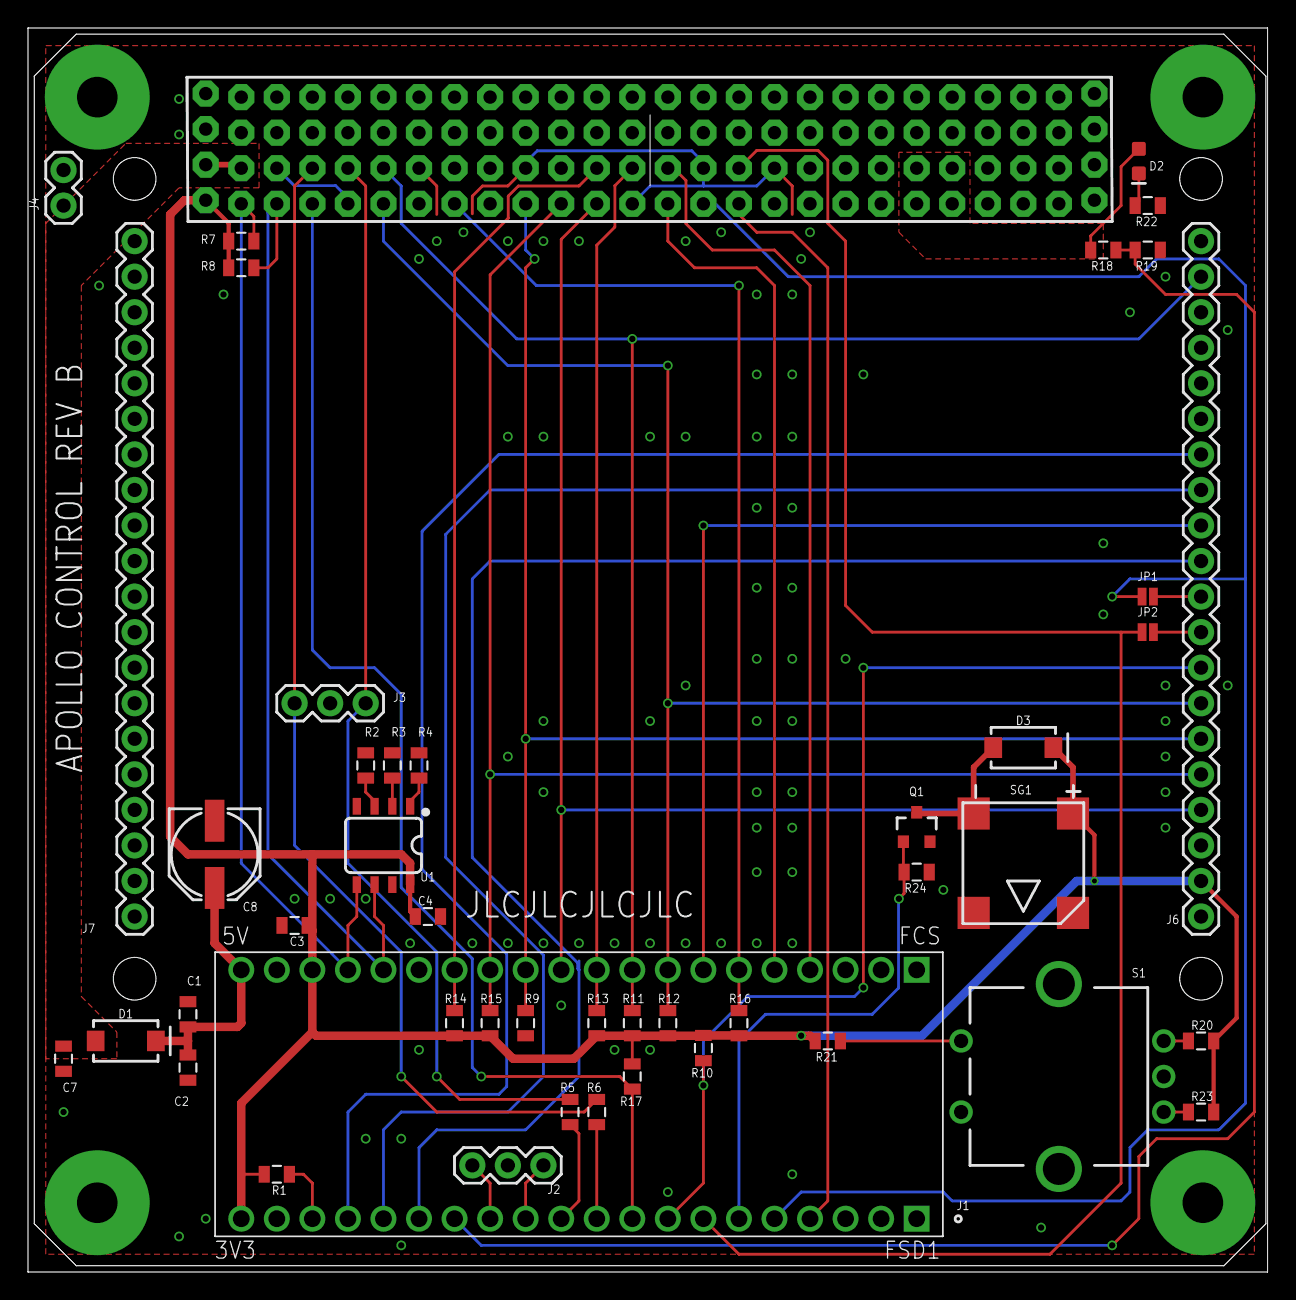
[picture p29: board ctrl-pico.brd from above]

Board: 2 copper layers, 88.6 x 88.9 mm, 47 parts (0 on the bottom side), 45 nets.

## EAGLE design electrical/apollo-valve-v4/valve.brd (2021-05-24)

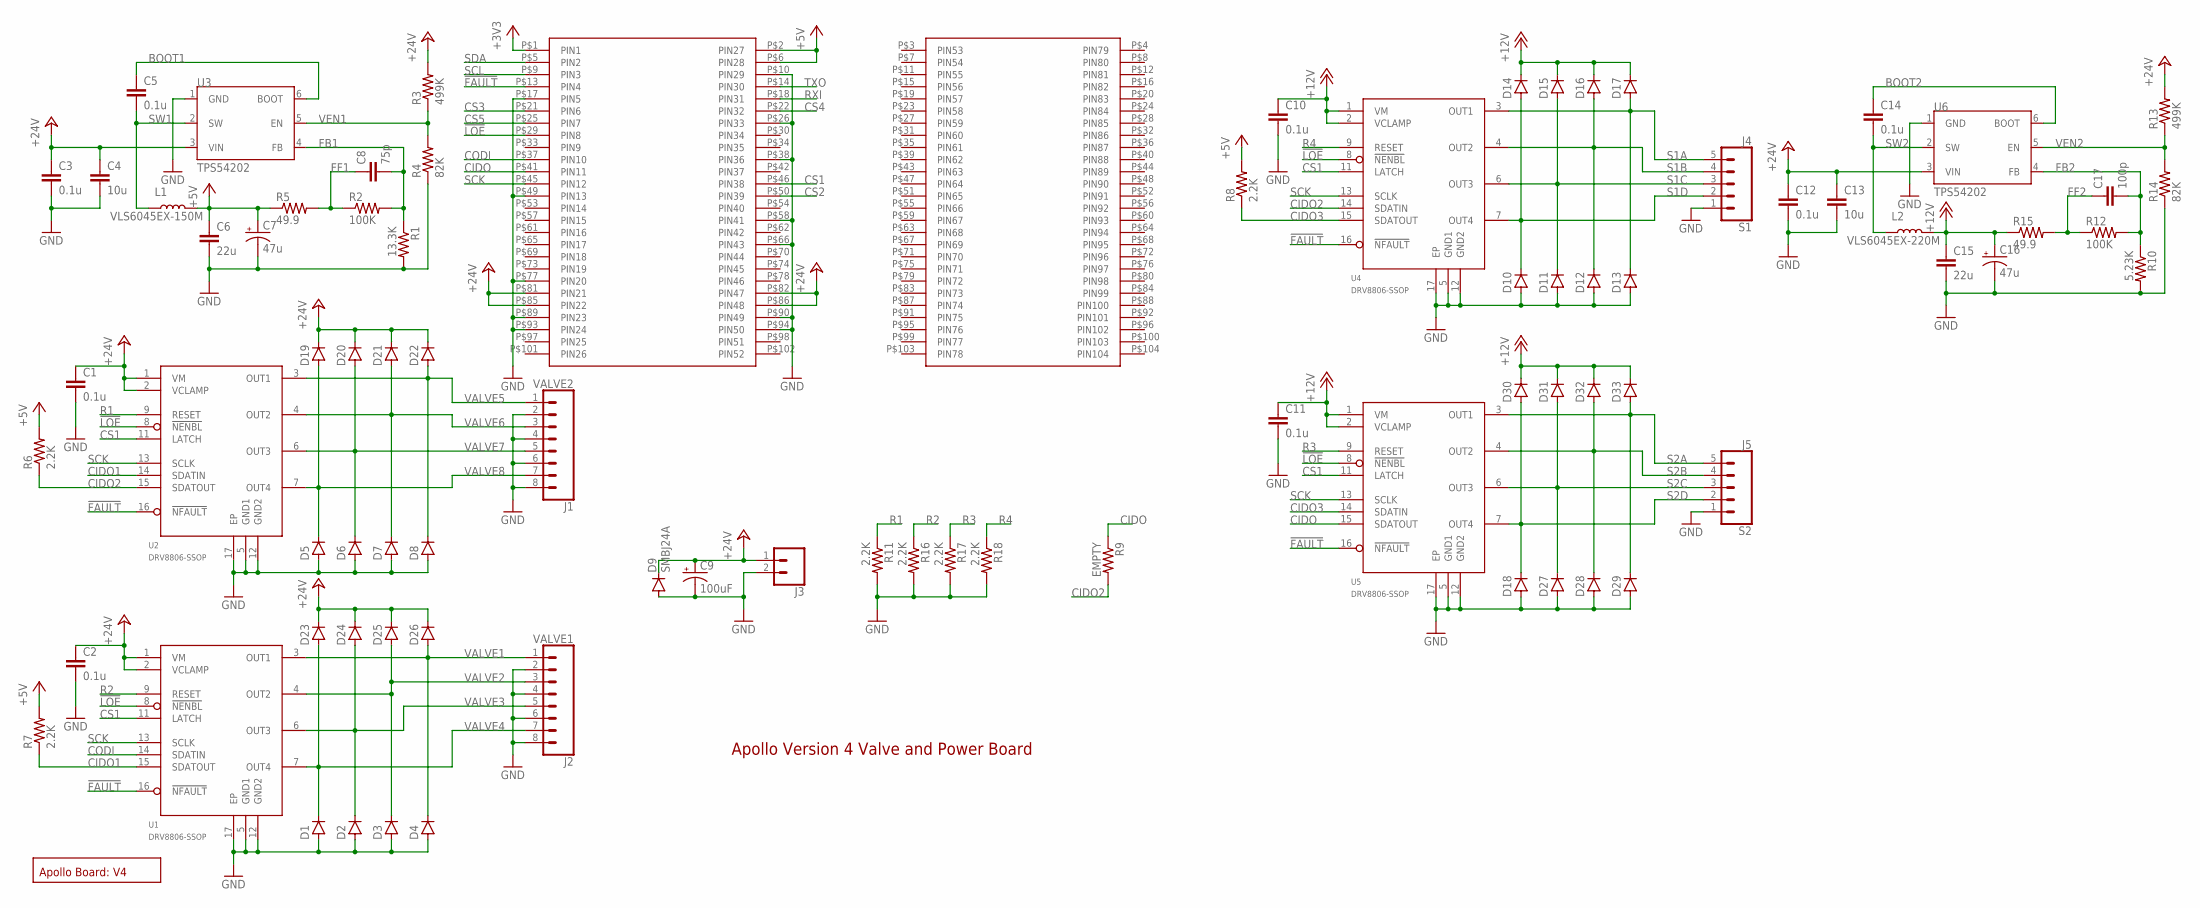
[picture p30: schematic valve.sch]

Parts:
C1, C2, C3, C5, C10, C11, C12, C14: 0.1u; 0805
C4, C13: 10u; 0805
C6, C15: 22u; 0805
C7, C16: 47u; PANASONIC_C
C8: 75p; 0805
C9: 100uF; PANASONIC_D
C17: 100p; 0805
D1, D2, D3, D4, D5, D6, D7, D8, D10, D11, D12, D13, D14, D15, D16, D17, D18, D19, D20, D21, D22, D23, D24, D25, D26, D27, D28, D29, D30, D31, D32, D33: B5819W; SOD123
D9: SMBJ24A; SMB
J1: VALVE2; SCREWTERMINAL-3.5MM-8
J2: VALVE1; SCREWTERMINAL-3.5MM-8
J3: CONN_023.5MM; SCREWTERMINAL-3.5MM-2
J4: S1; JST-5-PTH
J5: S2; JST-5-PTH
L1: VLS6045EX-150M; VLS6045EX
L2: VLS6045EX-220M; VLS6045EX
R1: 13.3K; 0805
R2, R12: 100K; 0805
R3, R13: 499K; 0805
R4, R14: 82K; 0805
R5, R15: 49.9; 0805
R6, R7, R8, R11, R16, R17, R18: 2.2K; 0805
R9: EMPTY; 0805
R10: 5.23K; 0805
U1, U2, U4, U5: DRV8806-SSOP; SOP65P640X120-17N
U3, U6: TPS54202; SOT23-6L
U$1: PC104_CONNECTOR
U$2: BOARD_TEMPLATE1; BOARD_TEMPLATE

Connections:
!FAULT!: U1.16 (!NFAULT), U2.16 (!NFAULT), U4.16 (!NFAULT), U5.16 (!NFAULT), U$1.P$13 (PIN4)
!LOE!: U1.8 (!NENBL), U2.8 (!NENBL), U4.8 (!NENBL), U5.8 (!NENBL), U$1.P$29 (PIN8)
+3V3: U$1.P$1 (PIN1)
+5V: C6.1, C7.+, L1.2, R5.1, R6.2, R7.2, R8.2, U$1.P$2 (PIN27), U$1.P$6 (PIN28)
+12V: C10.1, C11.1, C15.1, C16.+, D14.C, D15.C, D16.C, D17.C, D30.C, D31.C, D32.C, D33.C, L2.2, R15.1, U4.1 (VM), U4.2 (VCLAMP), U5.1 (VM), U5.2 (VCLAMP)
+24V: C1.1, C2.1, C3.1, C4.1, C9.+, C12.1, C13.1, D9.C, D19.C, D20.C, D21.C, D22.C, D23.C, D24.C, D25.C, D26.C, J3.1, R3.2, R13.2, U1.1 (VM), U1.2 (VCLAMP), U2.1 (VM), U2.2 (VCLAMP), U3.3 (VIN), U6.3 (VIN), U$1.P$81 (PIN21), U$1.P$82 (PIN47), U$1.P$85 (PIN22), U$1.P$86 (PIN48)
BOOT1: C5.1, U3.6 (BOOT)
BOOT2: C14.1, U6.6 (BOOT)
CIDO: R9.1, U5.15 (SDATOUT), U$1.P$41 (PIN11)
CIDO1: R7.1, U1.15 (SDATOUT), U2.14 (SDATIN)
CIDO2: R6.1, R9.2, U2.15 (SDATOUT), U4.14 (SDATIN)
CIDO3: R8.1, U4.15 (SDATOUT), U5.14 (SDATIN)
CODI: U1.14 (SDATIN), U$1.P$37 (PIN10)
CS1: U1.11 (LATCH), U2.11 (LATCH), U4.11 (LATCH), U5.11 (LATCH), U$1.P$46 (PIN38)
CS2: U$1.P$50 (PIN39)
CS3: U$1.P$21 (PIN6)
CS4: U$1.P$22 (PIN32)
CS5: U$1.P$25 (PIN7)
FB1: C8.2, R1.1, R2.2, U3.4 (FB)
FB2: C17.2, R10.1, R12.2, U6.4 (FB)
FF1: C8.1, R2.1, R5.2
FF2: C17.1, R12.1, R15.2
GND: C1.2, C2.2, C3.2, C4.2, C6.2, C7.-, C9.-, C10.2, C11.2, C12.2, C13.2, C15.2, C16.-, D1.A, D2.A, D3.A, D4.A, D5.A, D6.A, D7.A, D8.A, D9.A, D10.A, D11.A, D12.A, D13.A, D18.A, D27.A, D28.A, D29.A, J1.2, J1.4, J1.6, J1.8, J2.2, J2.4, J2.6, J2.8, J3.2, J4.1, J5.1, R1.2, R4.1, R10.2, R11.2, R14.1, R16.2, R17.2, R18.2, U1.5 (GND1), U1.12 (GND2), U1.17 (EP), U2.5 (GND1), U2.12 (GND2), U2.17 (EP), U3.1 (GND), U4.5 (GND1), U4.12 (GND2), U4.17 (EP), U5.5 (GND1), U5.12 (GND2), U5.17 (EP), U6.1 (GND), U$1.P$10 (PIN29), U$1.P$17 (PIN5), U$1.P$26 (PIN33), U$1.P$38 (PIN36), U$1.P$49 (PIN13), U$1.P$58 (PIN41), U$1.P$66 (PIN43), U$1.P$77 (PIN20), U$1.P$89 (PIN23), U$1.P$90 (PIN49), U$1.P$93 (PIN24), U$1.P$94 (PIN50)
R1: R11.1, U2.9 (RESET)
R2: R16.1, U1.9 (RESET)
R3: R17.1, U5.9 (RESET)
R4: R18.1, U4.9 (RESET)
RXI: U$1.P$18 (PIN31)
S1A: D13.C, D17.A, J4.5, U4.3 (OUT1)
S1B: D12.C, D16.A, J4.4, U4.4 (OUT2)
S1C: D11.C, D15.A, J4.3, U4.6 (OUT3)
S1D: D10.C, D14.A, J4.2, U4.7 (OUT4)
S2A: D29.C, D33.A, J5.5, U5.3 (OUT1)
S2B: D28.C, D32.A, J5.4, U5.4 (OUT2)
S2C: D27.C, D31.A, J5.3, U5.6 (OUT3)
S2D: D18.C, D30.A, J5.2, U5.7 (OUT4)
SCK: U1.13 (SCLK), U2.13 (SCLK), U4.13 (SCLK), U5.13 (SCLK), U$1.P$45 (PIN12)
SCL: U$1.P$9 (PIN3)
SDA: U$1.P$5 (PIN2)
SW1: C5.2, L1.1, U3.2 (SW)
SW2: C14.2, L2.1, U6.2 (SW)
TXO: U$1.P$14 (PIN30)
VALVE1: D4.C, D26.A, J2.1, U1.3 (OUT1)
VALVE2: D3.C, D25.A, J2.3, U1.4 (OUT2)
VALVE3: D2.C, D24.A, J2.5, U1.6 (OUT3)
VALVE4: D1.C, D23.A, J2.7, U1.7 (OUT4)
VALVE5: D8.C, D22.A, J1.1, U2.3 (OUT1)
VALVE6: D7.C, D21.A, J1.3, U2.4 (OUT2)
VALVE7: D6.C, D20.A, J1.5, U2.6 (OUT3)
VALVE8: D5.C, D19.A, J1.7, U2.7 (OUT4)
VEN1: R3.1, R4.2, U3.5 (EN)
VEN2: R13.1, R14.2, U6.5 (EN)

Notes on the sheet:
Apollo Version 4 Valve and Power Board

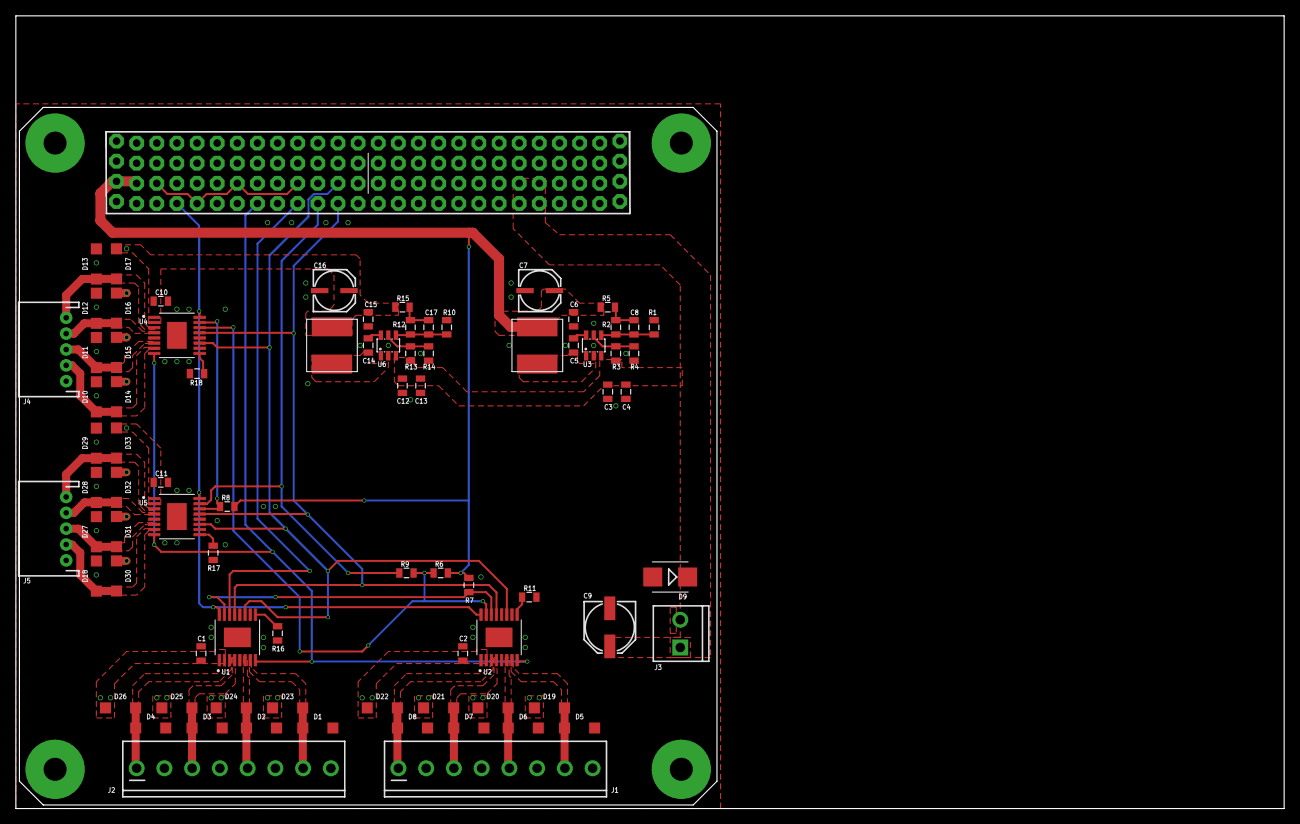
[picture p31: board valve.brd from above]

Board: 4 copper layers, 160.0 x 100.0 mm, 83 parts (0 on the bottom side), 43 nets.

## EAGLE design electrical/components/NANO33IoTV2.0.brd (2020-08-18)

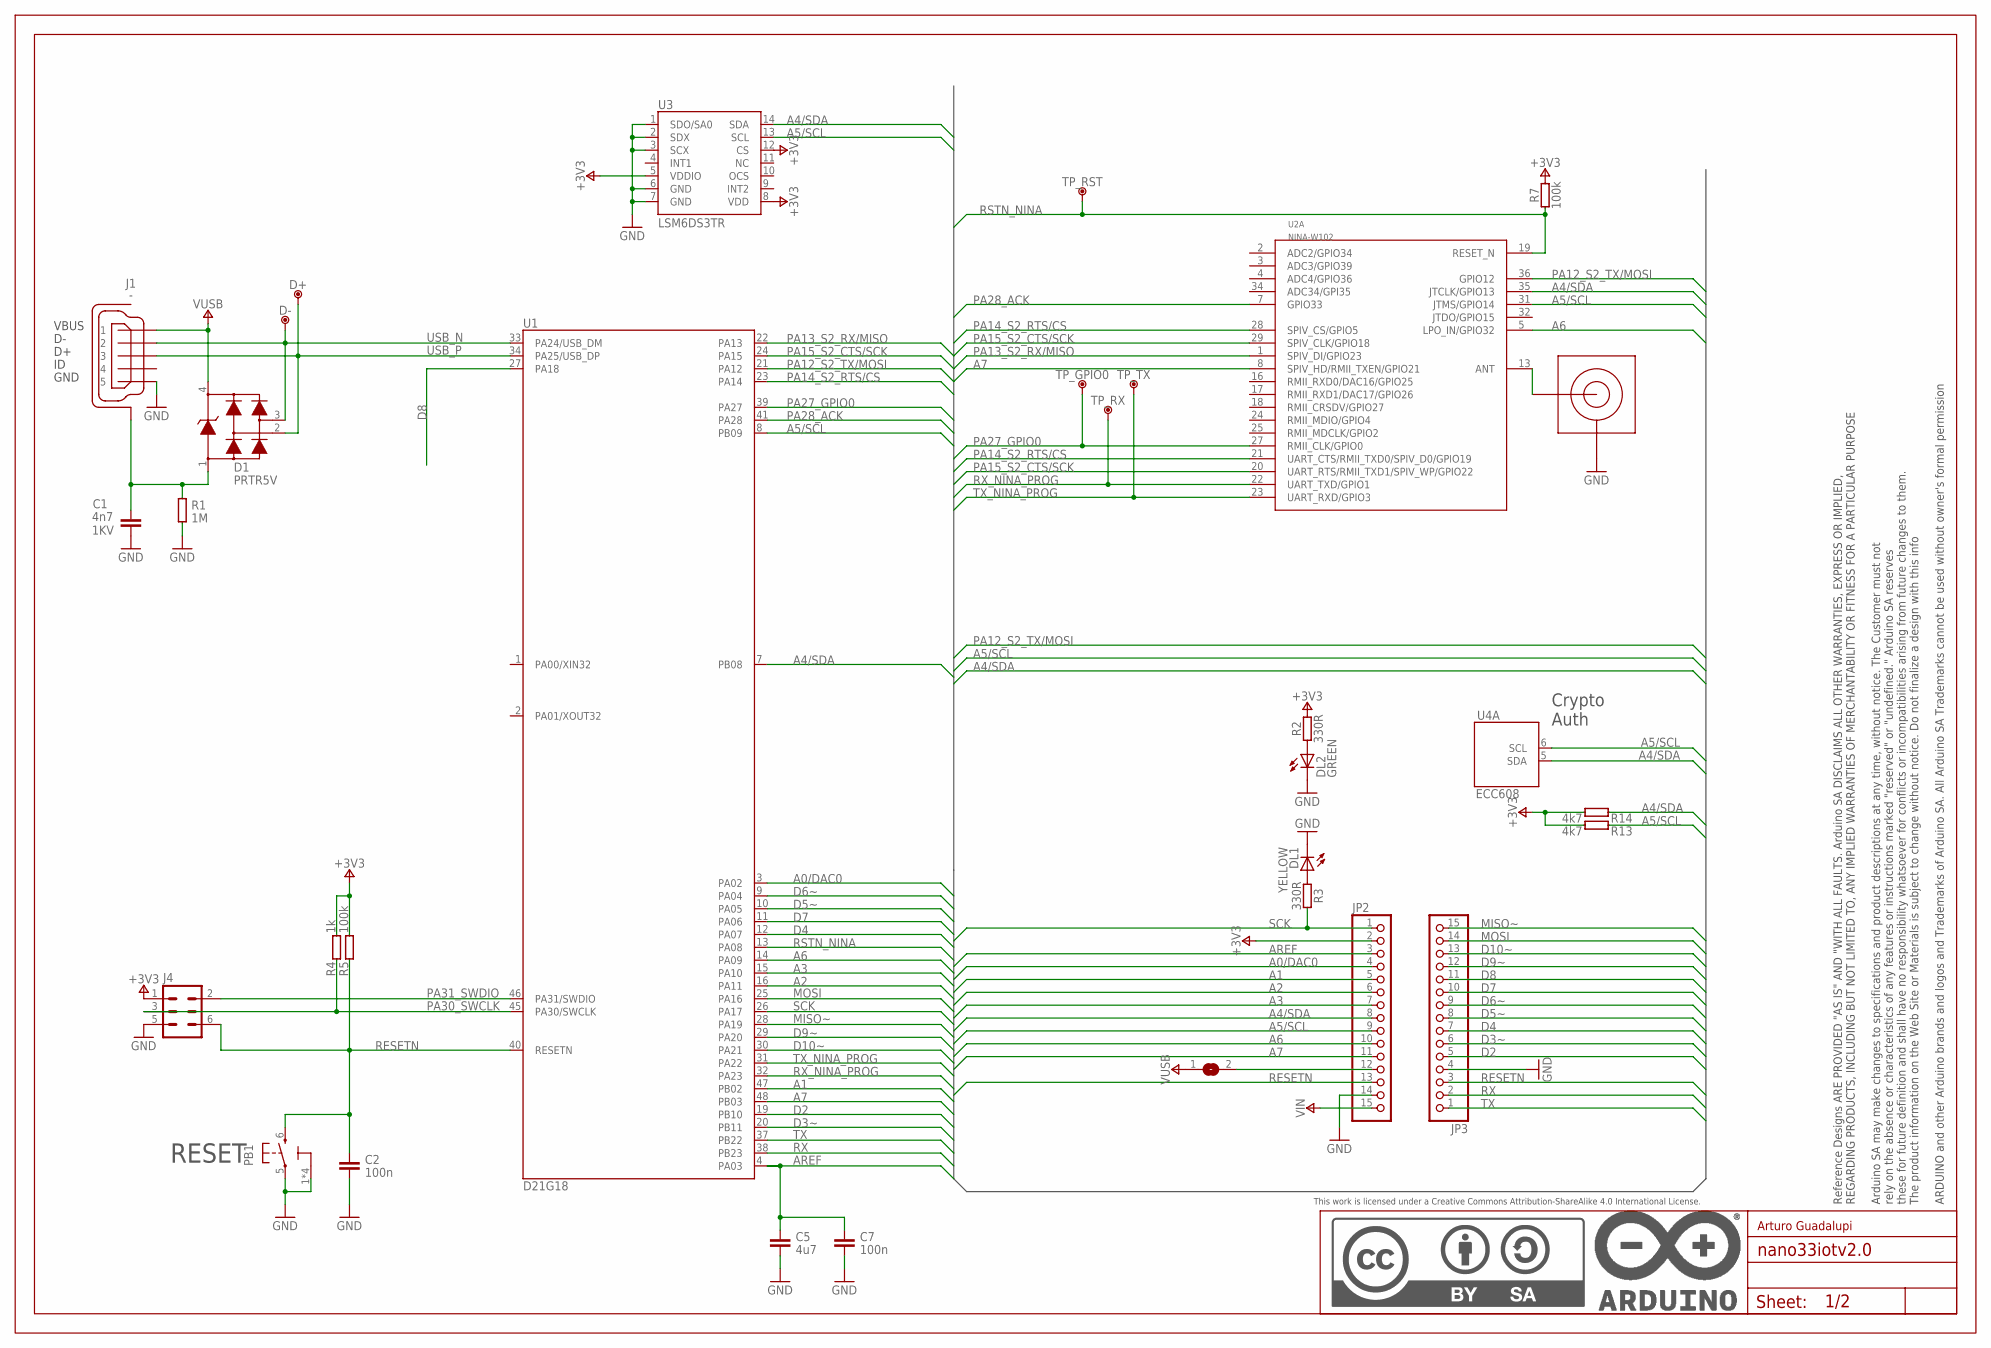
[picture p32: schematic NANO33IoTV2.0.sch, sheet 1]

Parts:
C1: 4n7; 0805-R2013X50N; VOLTAGE 1KV
C2, C7: 100n; 0402-1005X55N
C5: 4u7; 0402-1005X55N
D1: PRTR5V; SOT190P230X110-4N
D+: DNP; TP-1.00MM
D-: DNP; TP-1.00MM
DL1: YELLOW; LEDC1608X80N-AK
DL2: GREEN; LEDC1608X80N-AK
FRAME1: DNP; FRAME
J1: -; ZX62-AB-5PA
J3: DNP; U.FL-R-SMT-1(60)/NO_CREAM
J4: DNP; 2X03-TP1
JP2, JP3: PINHD-1X15-CASTELLATED; 1X15-CASTELL
PB1: PTS820; C&K_PTS820_NO_HOLES
R1: 1M; 0402-1005X55N
R2, R3: 330R; 0402-1005X55N
R4: 1k; 0402-1005X55N
R5, R7: 100k; 0402-1005X55N
R13, R14: 4k7; 0402-1005X55N
SJ1: DNP; SJ
TP_GPIO0: DNP; TP-0.8MM
TP_RST: DNP; TP-0.8MM
TP_RX: DNP; TP-0.8MM
TP_TX: DNP; TP-0.8MM
U1: D21G18; QFN50P700X700X90-49XN-EPSQ515
U2: NINA-W102; NINA-W1X
U3: LSM6DS3TR; LGA14L
U4: ECC608; SON50P300X200X60-9N-EP160X140

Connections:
+3V3: J4.1, JP2.2, R2.2, R4.2, R5.2, R7.2, R13.2, R14.2, U3.5 (VDDIO), U3.8 (VDD), U3.12 (CS); also elsewhere on the board
A0/DAC0: JP2.4, U1.3 (PA02)
A1: JP2.5, U1.47 (PB02)
A2: JP2.6, U1.16 (PA11)
A3: JP2.7, U1.15 (PA10)
A4/SDA: JP2.8, R14.1, U1.7 (PB08), U2.35 (JTCLK/GPIO13), U3.14 (SDA), U4.5 (SDA)
A5/SCL: JP2.9, R13.1, U1.8 (PB09), U2.31 (JTMS/GPIO14), U3.13 (SCL), U4.6 (SCL)
A6: JP2.10, U1.14 (PA09), U2.5 (LPO_IN/GPIO32)
A7: JP2.11, U1.48 (PB03), U2.8 (SPIV_HD/RMII_TXEN/GPIO21)
AREF: C5.1, C7.1, JP2.3, U1.4 (PA03)
D2: JP3.5, U1.19 (PB10)
D3~: JP3.6, U1.20 (PB11)
D4: JP3.7, U1.12 (PA07)
D5~: JP3.8, U1.10 (PA05)
D6~: JP3.9, U1.9 (PA04)
D7: JP3.10, U1.11 (PA06)
D8: JP3.11, U1.27 (PA18)
D9~: JP3.12, U1.29 (PA20)
D10~: JP3.13, U1.30 (PA21)
GND: C1.2, C2.2, C5.2, C7.2, DL1.C, DL2.C, J1.5, J3.GND1 (GND), J3.GND2 (GND), J4.5, JP2.14, JP3.4, PB1.1 (3), PB1.2 (3), PB1.3, PB1.4 (3), PB1.5 (1), R1.1, U3.1 (SDO/SA0), U3.2 (SDX), U3.3 (SCX), U3.6 (GND), U3.7 (GND); also elsewhere on the board
MISO~: JP3.15, U1.28 (PA19)
MOSI: JP3.14, U1.25 (PA16)
unnamed: C1.1, D1.1, J1.6 (SH), J1.7 (SH), J1.8 (SH), J1.9 (SH), J1.10 (SH), J1.11 (SH), R1.2
unnamed: DL2.A, R2.1
unnamed: DL1.A, R3.1
unnamed: J3.SIG, U2.13 (ANT)
unnamed: JP2.12, SJ1.2
PA12_S2_TX/MOSI: U1.21 (PA12), U2.36 (GPIO12)
PA13_S2_RX/MISO: U1.22 (PA13), U2.1 (SPIV_DI/GPIO23)
PA14_S2_RTS/CS: U1.23 (PA14), U2.21 (UART_CTS/RMII_TXD0/SPIV_D0/GPIO19), U2.28 (SPIV_CS/GPIO5)
PA15_S2_CTS/SCK: U1.24 (PA15), U2.20 (UART_RTS/RMII_TXD1/SPIV_WP/GPIO22), U2.29 (SPIV_CLK/GPIO18)
PA27_GPIO0: TP_GPIO0.X, U1.39 (PA27), U2.27 (RMII_CLK/GPIO0)
PA28_ACK: U1.41 (PA28), U2.7 (GPIO33)
PA30_SWCLK: J4.3, R4.1, U1.45 (PA30/SWCLK)
PA31_SWDIO: J4.2, U1.46 (PA31/SWDIO)
RESETN: C2.1, J4.6, JP2.13, JP3.3, PB1.6 (2), R5.1, U1.40 (RESETN)
RSTN_NINA: R7.1, TP_RST.X, U1.13 (PA08), U2.19 (RESET_N)
RX: JP3.2, U1.38 (PB23)
RX_NINA_PROG: TP_RX.X, U1.32 (PA23), U2.22 (UART_TXD/GPIO1)
SCK: JP2.1, R3.2, U1.26 (PA17)
TX: JP3.1, U1.37 (PB22)
TX_NINA_PROG: TP_TX.X, U1.31 (PA22), U2.23 (UART_RXD/GPIO3)
USB_N: D1.3, D-.X, J1.2, U1.33 (PA24/USB_DM)
USB_P: D1.2, D+.X, J1.3, U1.34 (PA25/USB_DP)
VIN: JP2.15; also elsewhere on the board
VUSB: D1.4, J1.1, SJ1.1; also elsewhere on the board

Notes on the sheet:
RESET
Crypto Auth
Arturo Guadalupi

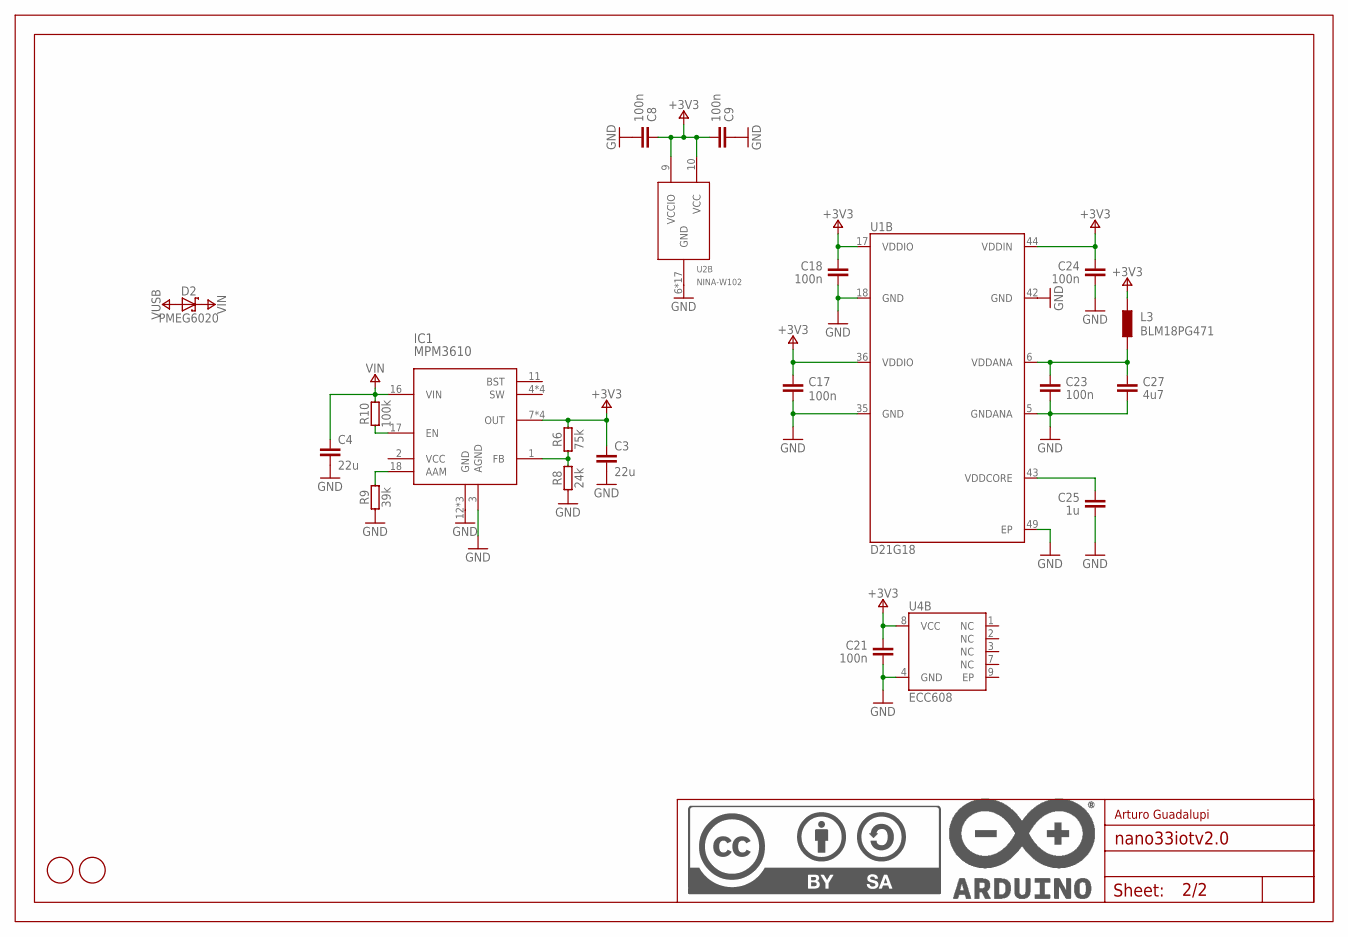
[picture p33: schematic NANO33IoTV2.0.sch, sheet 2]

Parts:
C3, C4: 22u; 0805-R2013X50N
C8, C9, C17, C18, C21, C23, C24: 100n; 0402-1005X55N
C25: 1u; 0402-1005X55N
C27: 4u7; 0603-1608X90N
D2: PMEG6020; SODFL3517X110N
FD1, FD2: DNP; FD-1-1.5
IC1: MPM3610
L3: BLM18PG471; 0603-1608X90N
R6: 75k; 0402-1005X55N
R8: 24k; 0402-1005X55N
R9: 39k; 0402-1005X55N
R10: 100k; 0402-1005X55N
U1: D21G18; QFN50P700X700X90-49XN-EPSQ515
U2: NINA-W102; NINA-W1X
U4: ECC608; SON50P300X200X60-9N-EP160X140
U$1: DNP; FRAME

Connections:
+3V3: C3.1, C8.1, C9.2, C17.1, C18.1, C21.1, C24.1, IC1.7 (OUT), IC1.8 (OUT), IC1.9 (OUT), IC1.20 (OUT), L3.1, R6.2, U1.17 (VDDIO), U1.36 (VDDIO), U1.44 (VDDIN), U2.9 (VCCIO), U2.10 (VCC), U4.8 (VCC); also elsewhere on the board
GND: C3.2, C4.2, C8.2, C9.1, C17.2, C18.2, C21.2, C23.2, C24.2, C25.2, C27.2, IC1.3 (AGND), IC1.12 (GND), IC1.13 (GND), IC1.14 (GND), R8.1, R9.1, U1.5 (GNDANA), U1.18 (GND), U1.35 (GND), U1.42 (GND), U1.49 (EP), U2.6 (GND), U2.12 (GND), U2.14 (GND), U2.26 (GND), U2.30 (GND), U2.GND@1 (GND), U2.GND@2 (GND), U2.GND@3 (GND), U2.GND@4 (GND), U2.GND@5 (GND), U2.GND@6 (GND), U2.GND@7 (GND), U2.GND@8 (GND), U2.GND@9 (GND), U2.GND@10 (GND), U2.GND@11 (GND), U2.GND@12 (GND), U4.4 (GND); also elsewhere on the board
N17852357: C23.1, C27.1, L3.2, U1.6 (VDDANA)
N17852431: C25.1, U1.43 (VDDCORE)
unnamed: IC1.1 (FB), R6.1, R8.2
unnamed: IC1.18 (AAM), R9.2
unnamed: IC1.17 (EN), R10.1
VIN: C4.1, D2.C, IC1.16 (VIN), R10.2; also elsewhere on the board
VUSB: D2.A; also elsewhere on the board

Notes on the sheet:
Arturo Guadalupi

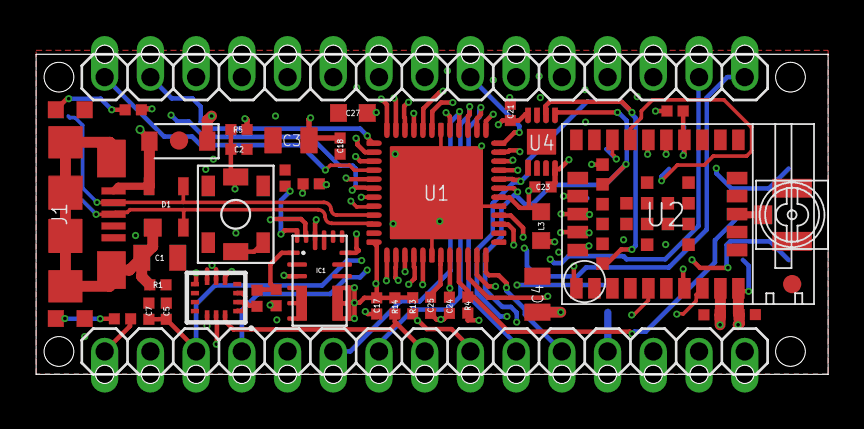
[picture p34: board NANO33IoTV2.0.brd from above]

Board: 4 copper layers, 44.0 x 17.8 mm, 54 parts (1 on the bottom side), 51 nets.

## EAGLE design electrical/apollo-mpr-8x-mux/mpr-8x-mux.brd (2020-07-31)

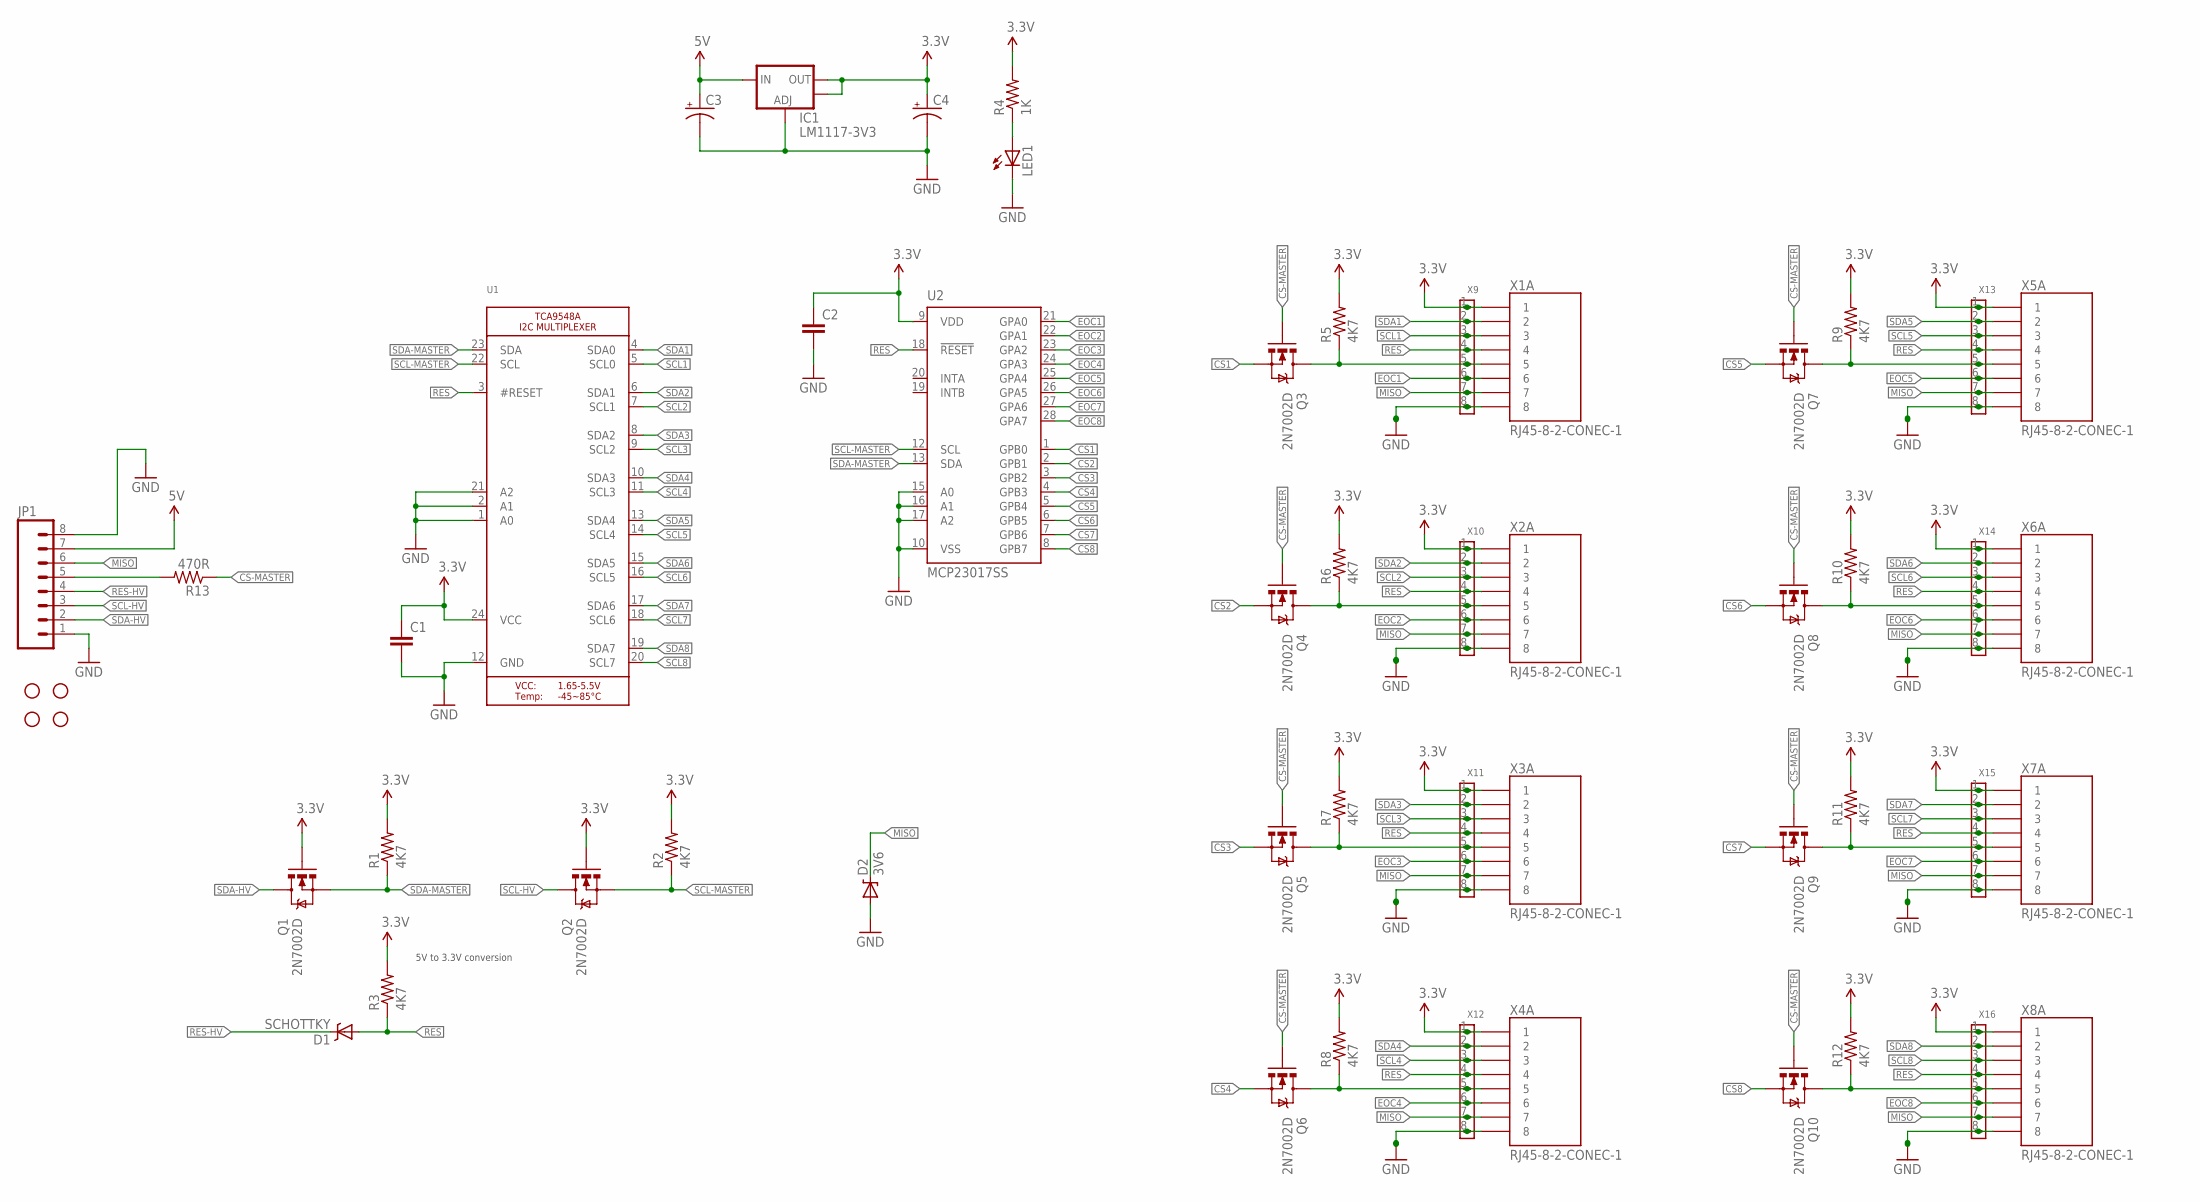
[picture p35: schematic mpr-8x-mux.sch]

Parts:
C1, C2: CAP0805; 0805
C3, C4: CAP_POL1206-KIT; EIA3216-KIT
D1: SCHOTTKY; SOD-323
D2: 3V6; SOD-323
IC1: LM1117-3V3; SOT223
JP1: M081X08; 1X08
JP2, JP3, JP4, JP5: STAND-OFF
LED1: LED0603; LED-0603
Q1, Q2, Q3, Q4, Q5, Q6, Q7, Q8, Q9, Q10: 2N7002D; SOT23-3
R1, R2, R3, R5, R6, R7, R8, R9, R10, R11, R12: 4K7; 0805
R4: 1K; 0805
R13: 470R; 0805
U1: TCA9548A; TSSOP24
U2: MCP23017SS; SSOP28
X1, X2, X3, X4, X5, X6, X7, X8: RJ45-8-2-CONEC-1; CONEC-33TS3004ST-88001
X9, X10, X11, X12, X13, X14, X15, X16: TP-GROUP-X8-2X04; 2X4

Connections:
3.3V: C1.1, C2.1, C4.A (+), IC1.2 (OUT), IC1.4 (OUT), Q1.1 (G), Q2.1 (G), R1.2, R2.2, R3.2, R4.2, R5.2, R6.2, R7.2, R8.2, R9.2, R10.2, R11.2, R12.2, U1.24 (VCC), U2.9 (VDD), X1.1, X2.1, X3.1, X4.1, X5.1, X6.1, X7.1, X8.1, X9.1, X10.1, X11.1, X12.1, X13.1, X14.1, X15.1, X16.1
5V: C3.A (+), IC1.3 (IN), JP1.7
CS1: Q3.2 (S), U2.1 (GPB0)
CS2: Q4.2 (S), U2.2 (GPB1)
CS3: Q5.2 (S), U2.3 (GPB2)
CS4: Q6.2 (S), U2.4 (GPB3)
CS5: Q7.2 (S), U2.5 (GPB4)
CS6: Q8.2 (S), U2.6 (GPB5)
CS7: Q9.2 (S), U2.7 (GPB6)
CS8: Q10.2 (S), U2.8 (GPB7)
CS-MASTER: Q3.1 (G), Q4.1 (G), Q5.1 (G), Q6.1 (G), Q7.1 (G), Q8.1 (G), Q9.1 (G), Q10.1 (G), R13.1
EOC1: U2.21 (GPA0), X1.6, X9.6
EOC2: U2.22 (GPA1), X2.6, X10.6
EOC3: U2.23 (GPA2), X3.6, X11.6
EOC4: U2.24 (GPA3), X4.6, X12.6
EOC5: U2.25 (GPA4), X5.6, X13.6
EOC6: U2.26 (GPA5), X6.6, X14.6
EOC7: U2.27 (GPA6), X7.6, X15.6
EOC8: U2.28 (GPA7), X8.6, X16.6
GND: C1.2, C2.2, C3.C (-), C4.C (-), D2.2 (A), IC1.1 (ADJ), JP1.1, JP1.8, LED1.C, U1.1 (A0), U1.2 (A1), U1.12 (GND), U1.21 (A2), U2.10 (VSS), U2.15 (A0), U2.16 (A1), U2.17 (A2), X1.8, X1.M1, X1.M2, X2.8, X2.M1, X2.M2, X3.8, X3.M1, X3.M2, X4.8, X4.M1, X4.M2, X5.8, X5.M1, X5.M2, X6.8, X6.M1, X6.M2, X7.8, X7.M1, X7.M2, X8.8, X8.M1, X8.M2, X9.8, X10.8, X11.8, X12.8, X13.8, X14.8, X15.8, X16.8
MISO: D2.1 (C), JP1.6, X1.7, X2.7, X3.7, X4.7, X5.7, X6.7, X7.7, X8.7, X9.7, X10.7, X11.7, X12.7, X13.7, X14.7, X15.7, X16.7
unnamed: LED1.A, R4.1
unnamed: Q7.3 (D), R9.1, X5.5, X13.5
unnamed: Q8.3 (D), R10.1, X6.5, X14.5
unnamed: Q9.3 (D), R11.1, X7.5, X15.5
unnamed: Q10.3 (D), R12.1, X8.5, X16.5
unnamed: Q6.3 (D), R8.1, X4.5, X12.5
unnamed: Q5.3 (D), R7.1, X3.5, X11.5
unnamed: Q4.3 (D), R6.1, X2.5, X10.5
unnamed: Q3.3 (D), R5.1, X1.5, X9.5
unnamed: JP1.5, R13.2
RES: D1.2 (A), R3.1, U1.3 (#RESET), U2.18 (!RESET), X1.4, X2.4, X3.4, X4.4, X5.4, X6.4, X7.4, X8.4, X9.4, X10.4, X11.4, X12.4, X13.4, X14.4, X15.4, X16.4
RES-HV: D1.1 (C), JP1.4
SCL1: U1.5 (SCL0), X1.3, X9.3
SCL2: U1.7 (SCL1), X2.3, X10.3
SCL3: U1.9 (SCL2), X3.3, X11.3
SCL4: U1.11 (SCL3), X4.3, X12.3
SCL5: U1.14 (SCL4), X5.3, X13.3
SCL6: U1.16 (SCL5), X6.3, X14.3
SCL7: U1.18 (SCL6), X7.3, X15.3
SCL8: U1.20 (SCL7), X8.3, X16.3
SCL-HV: JP1.3, Q2.3 (D)
SCL-MASTER: Q2.2 (S), R2.1, U1.22 (SCL), U2.12 (SCL)
SDA1: U1.4 (SDA0), X1.2, X9.2
SDA2: U1.6 (SDA1), X2.2, X10.2
SDA3: U1.8 (SDA2), X3.2, X11.2
SDA4: U1.10 (SDA3), X4.2, X12.2
SDA5: U1.13 (SDA4), X5.2, X13.2
SDA6: U1.15 (SDA5), X6.2, X14.2
SDA7: U1.17 (SDA6), X7.2, X15.2
SDA8: U1.19 (SDA7), X8.2, X16.2
SDA-HV: JP1.2, Q1.3 (D)
SDA-MASTER: Q1.2 (S), R1.1, U1.23 (SDA), U2.13 (SDA)

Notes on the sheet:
5V to 3.3V conversion

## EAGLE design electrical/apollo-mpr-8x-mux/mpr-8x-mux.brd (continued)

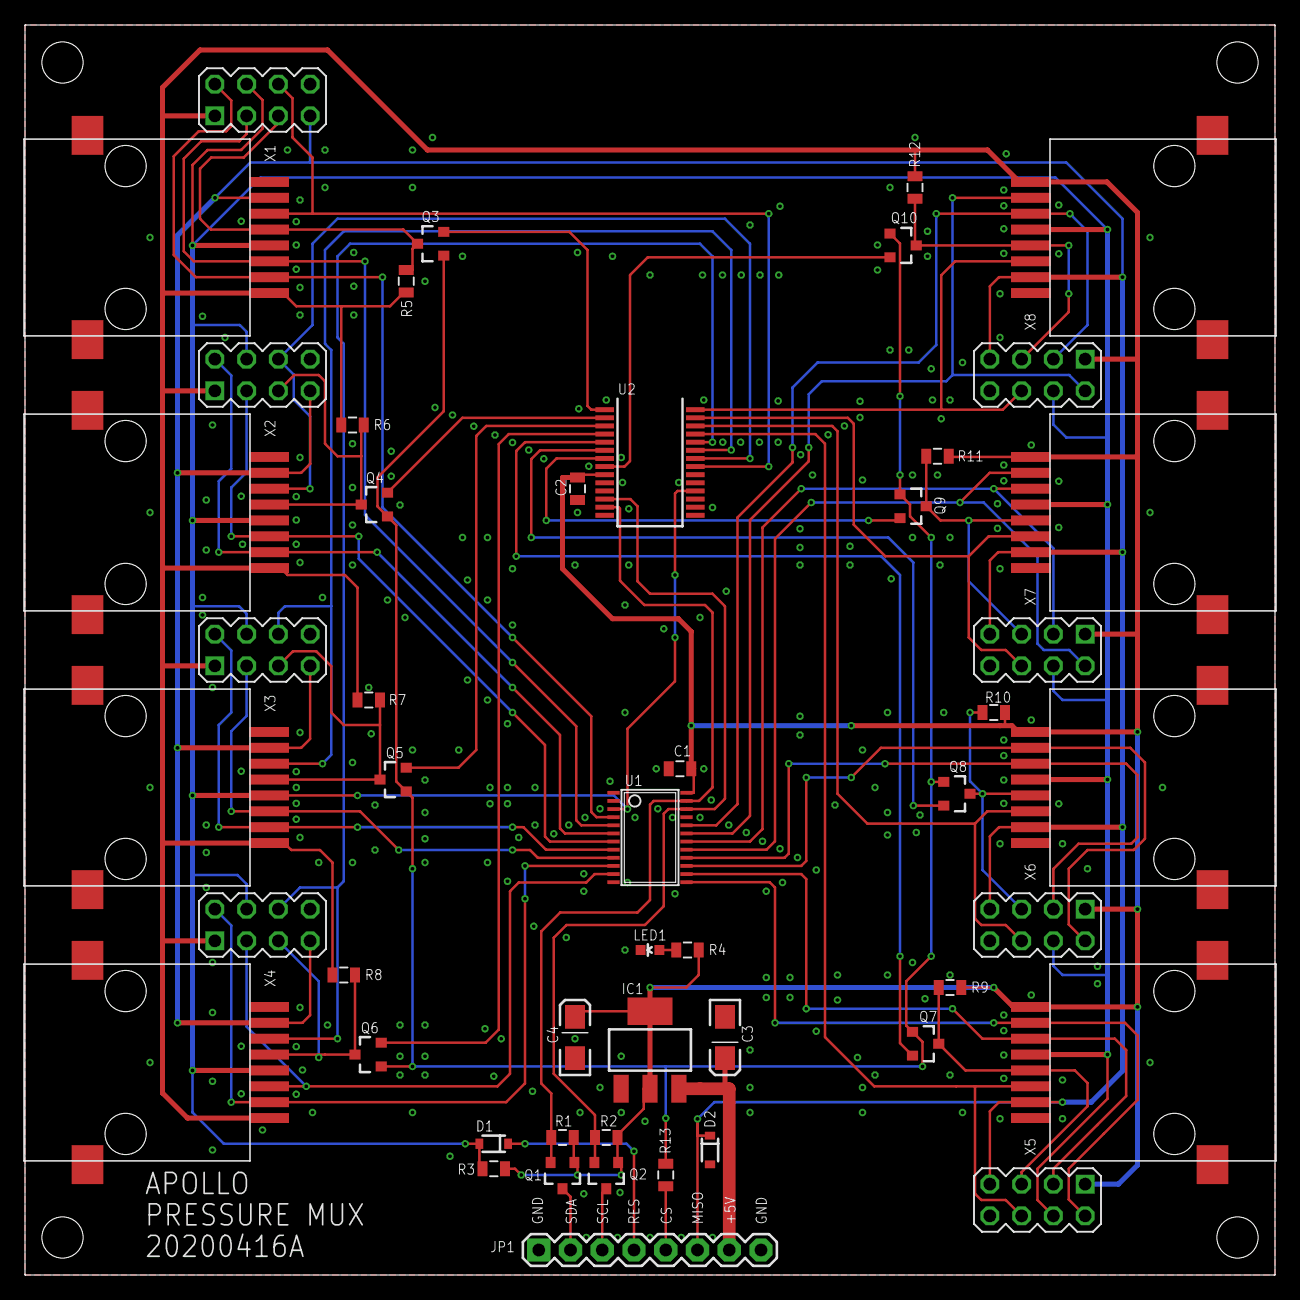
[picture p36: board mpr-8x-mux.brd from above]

Board: 2 copper layers, 100.0 x 100.0 mm, 54 parts (0 on the bottom side), 53 nets.

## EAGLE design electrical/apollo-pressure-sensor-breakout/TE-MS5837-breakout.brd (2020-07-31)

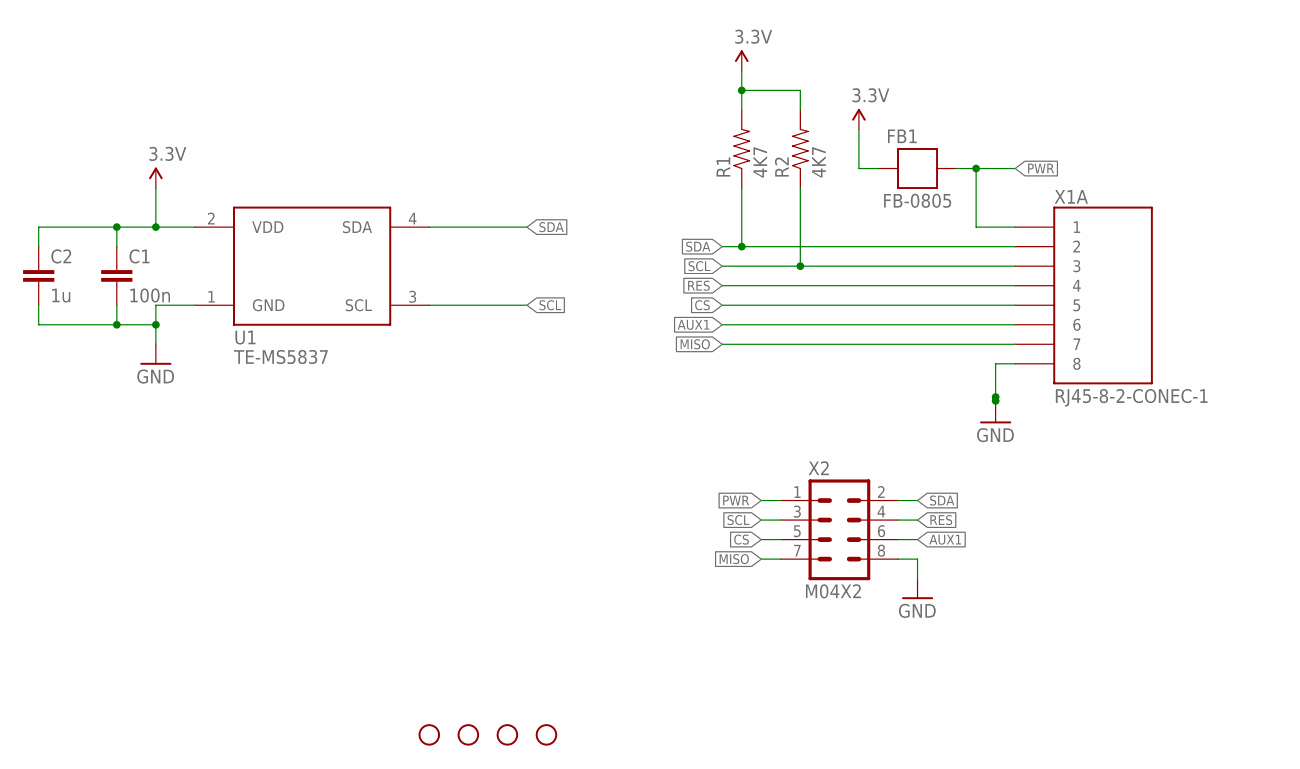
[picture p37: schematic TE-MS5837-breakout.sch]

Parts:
C1: 100n; 0805
C2: 1u; 0805
FB1: FB-0805; 0805
JP1, JP2, JP3, JP4: STAND-OFF
R1, R2: 4K7; 0805
U1: TE-MS5837
X1: RJ45-8-2-CONEC-1; CONEC-33TS3004ST-88001
X2: M04X2; 2X4

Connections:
3.3V: C1.1, C2.1, FB1.2, R1.2, R2.2, U1.2 (VDD)
AUX1: X1.6, X2.6
CS: X1.5, X2.5
GND: C1.2, C2.2, U1.1 (GND), X1.8, X1.M1, X1.M2, X2.8
MISO: X1.7, X2.7
PWR: FB1.1, X1.1, X2.1
RES: X1.4, X2.4
SCL: R2.1, U1.3 (SCL), X1.3, X2.3
SDA: R1.1, U1.4 (SDA), X1.2, X2.2


Board: 2 copper layers, 26.0 x 37.0 mm, 14 parts (0 on the bottom side), 9 nets.

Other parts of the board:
JP5, JP6: STAND-OFF

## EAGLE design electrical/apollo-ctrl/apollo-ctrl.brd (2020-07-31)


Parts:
BAT1: BATTERYAA-KIT; BATTERY-AA-KIT
C1: > 47u; CPOL-RADIAL-1000UF-25V
COIL1, COIL2: M023.5MM; SCREWTERMINAL-3.5MM-2
D1, D10, D11, D12: 3V6; DIODE-1N4148
D2, D4, D5: DIODE-SCHOTTKYPTH; DIODE-1N4001
D3: ZENER 13V; DO201-15
D6, D7, D8, D9: DIODE1N4148; DIODE-1N4148
F1: FUSE 3A; FUSE-KEYSTONE-3568
F2, F3: PTC
JP1, JP2, JP3, JP4: STAND-OFF
LED1: GRN; LED5MM
LED2: RED; LED5MM
LOGO1: APOLLO-LOGO
OK1, OK2: PC817; DIL04
Q1, Q2: N-chan; TO220V
R1: 470R 500mW; AXIAL-0.5
R2, R6, R9: 10K; AXIAL-0.4
R3, R7, R8, R10, R11, R12, R13, R14, R15: 620R; AXIAL-0.4
R4, R5: 4K7; AXIAL-0.4
S1: TAC_SWITCHPTH; TACTILE-PTH
SG1: BUZZER; BUZZER-AI-3035
SG2, SG3, SG4: BUZZER; 1X01NS
SJ1, SJ2: SOLDERJUMPERNO; SJ_2S-NO
SJ3, SJ4: SOLDERJUMPER_2WAYS; SJ_3
TVS1, TVS2, TVS3, TVS4, TVS5, TVS6, TVS7: TVS 16V; DIODE-1N4148
U1: NANO
U2: ADAFRUIT-MPRLS
X1: BARREL-JACK; POWER_JACK_PTH
X2: SENSOR-O2; JST-PH-4-VERT
X3: M081X08; 1X08
X4: FAN; 1X02
X5, X6: M03PTH; 1X03

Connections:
3.3V: R4.P$2 (2), R5.P$2 (2), SJ3.3, SJ4.3, U1.3.3V
5V: D4.C, SJ3.1, SJ4.1, U1.5V, U2.VIN, X2.4 (VCC), X3.7
+12V: C1.1 (+), COIL1.2, COIL2.2, D5.C, D6.C, D8.C, R1.P$2 (2), TVS1.C, TVS3.C, U1.RAW (VBAT), X4.1
A0: SJ2.1, U1.A0
A6: U1.A6, X5.1
A7: U1.A7, X6.1
AUX1: SJ1.1, U1.D12 (D12/MOSI), X3.4
AUX2: U1.A1, X3.5
AUX3: U1.A2, X3.6
BUTTON: S1.1, S1.2, TVS5.C, U1.D11 (D11/MISO)
BUZZ: SG1.P, SG2.1, SG3.1, SG4.1, U1.D8 (D8/ICP1)
COIL-1: R6.P$2 (2), R7.P$1 (1), U1.D4
COIL-1-CHECK: OK1.4 (COL), U1.D5 (D5/OC0B)
COIL-2: R9.P$2 (2), R10.P$1 (1), U1.D6 (D6/OC0A)
COIL-2-CHECK: OK2.4 (COL), U1.D7
GND: BAT1.GND@1 (-), C1.2 (-), D1.A, D3.A, D10.A, D11.A, D12.A, LED1.K (C), LED2.K (C), OK1.2 (C), OK1.3 (EMIT), OK2.2 (C), OK2.3 (EMIT), Q1.3 (S), Q2.3 (S), R3.P$1 (1), R6.P$1 (1), R9.P$1 (1), S1.3, S1.4, SG1.N, TVS1.A, TVS2.A, TVS3.A, TVS4.A, TVS5.A, TVS6.A, TVS7.A, U1.GND, U1.GND1 (GND2), U2.GND, X1.GND, X1.GNDBREAK, X2.1 (GND), X3.1, X3.8, X4.2, X5.3, X6.3
LED-G: R12.P$2 (2), U1.D10 (D10/OC1B)
LED-R: R13.P$2 (2), U1.D9 (D9/OC1A)
MCU-TO-O2: R15.P$2 (2), U1.D2 (D2/INT0)
unnamed: SJ1.2, U2.RST
unnamed: F2.1, Q1.2 (D)
unnamed: Q1.1 (G), R7.P$2 (2)
unnamed: OK1.1 (A), R8.P$2 (2)
unnamed: COIL1.1, D6.A, D7.A, F2.2, TVS2.C
unnamed: F1.1A, F1.1B, X1.PWR
unnamed: D7.C, R8.P$1 (1)
unnamed: OK2.1 (A), R11.P$2 (2)
unnamed: Q2.1 (G), R10.P$2 (2)
unnamed: COIL2.1, D8.A, D9.A, F3.2, TVS4.C
unnamed: F3.1, Q2.2 (D)
unnamed: D9.C, R11.P$1 (1)
unnamed: D3.C, D5.A, F1.2A, F1.2B, R2.P$2 (2)
unnamed: BAT1.PWR@1 (+), D2.C, D4.A
unnamed: LED2.A, R13.P$1 (1)
unnamed: LED1.A, R12.P$1 (1)
unnamed: R14.P$1 (1), TVS6.C, X2.2 (TX)
unnamed: R15.P$1 (1), TVS7.C, X2.3 (RX)
unnamed: D1.C, D2.A, R1.P$1 (1)
unnamed: SJ2.2, U2.EOC
unnamed: SJ4.2, X6.2
unnamed: SJ3.2, X5.2
O2-TO-MCU: R14.P$2 (2), U1.D3 (D3/INT1/OC2B)
SCL: D10.C, R4.P$1 (1), U1.A5 (A5/SCL), U2.SCL, X3.3
SDA: D11.C, R5.P$1 (1), U1.A4 (A4/SDA), U2.SDA, X3.2
V-MON: D12.C, R2.P$1 (1), R3.P$2 (2), U1.A3

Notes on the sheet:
poor-man's battery charger treats the battery like a super-cap use Li-Ion only! 14500 cell 2.8V to 4.2V
continuity checker
power fail detection
backup power diode-OR
over-voltage and reverse polarity protection
flyback
detects if coil is open or fuse is blown
spare I2C header
zener diodes for I2C optional
pull-up resistors for I2C optional
optional connects D12 to RST



Board: 2 copper layers, 100.0 x 80.0 mm, 69 parts (4 on the bottom side), 45 nets.

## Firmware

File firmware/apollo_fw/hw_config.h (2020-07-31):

#ifndef _HW_CONFIG_H_
#define _HW_CONFIG_H_

#include <stdint.h>

#define PIN_LED_RED        9
#define PIN_LED_GREEN      10
#define PIN_BUTTON         11
#define PIN_BUZZER         8

#define PIN_COIL_1         4
#define PIN_COIL_2         6
#define PIN_COILCHECK_1    5
#define PIN_COILCHECK_2    7

#define PIN_O2SENS_RX      3
#define PIN_O2SENS_TX      2
#define OXY_HW_TIMEOUT_LONG    10000 // max time for oxygen sensor to boot
#define OXY_HW_TIMEOUT_SHORT   3000  // max time between oxygen sensor data packets

#define PIN_12V_MONITOR    A3
#define VMON_R1            10000 // resistor value for voltage divider
#define VMON_R2            620   // resistor value for voltage divider
#define VMON_THRESH_LOW    10000 // undervoltage limit in mV
#define VMON_THRESH_HIGH   13000 // overvoltage  limit in mV
#define VMON_THRESH_HYSTER 500   // hysteresis         in mV

#define PIN_COIL_5WAY      PIN_COIL_1
#define PIN_COIL_2WAY      PIN_COIL_2
#define PIN_COILCHECK_5WAY PIN_COILCHECK_1
#define PIN_COILCHECK_2WAY PIN_COILCHECK_2

#define COIL_SETTLE_TIME   500 // physical time for solenoid to move, and for the back-EMF to dissipate

#define PIN_I2C_SCL        A5
#define PIN_I2C_SDA        A4

#define I2CADDR_TCA9548A (0x70 << 1)
#define I2CADDR_MCP23017 (0x20 << 1)
#define I2CADDR_MPR      (0x18 << 1)
#define PRESSURE_SENSOR_MAX_CNT    8

#define PIN_MPR_RST        12
#define PIN_MPR_EOC        A0
#define PIN_AUX2           A1
#define PIN_AUX3           A2

#define PIN_DAUGHTER_CS   PIN_AUX2
#define PIN_DAUGHTER_MOSI PIN_AUX3

#define SPI_BITBANG_DLY    1 // bit delay (microseconds) for SPI bit-bang, might need to be long as the bus is open-drain (shared with I2C)
#define MPR_SAMPLE_TIME    200 // time (milliseconds) to wait for MPR samples, minimum is 5

// if a feature is simply not available, disable it here so it does not cause problems
#define USE_OXY_SENSOR
#define USE_PRESSURE_SENSOR
#define USE_COIL_CHECK
#define USE_VOLTAGE_MONITOR

#endif

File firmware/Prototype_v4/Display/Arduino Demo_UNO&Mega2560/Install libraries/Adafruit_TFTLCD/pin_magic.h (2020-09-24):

#ifndef _pin_magic_
#define _pin_magic_

// This header file serves two purposes:
//
// 1) Isolate non-portable MCU port- and pin-specific identifiers and
//    operations so the library code itself remains somewhat agnostic
//    (PORTs and pin numbers are always referenced through macros).
//
// 2) GCC doesn't always respect the "inline" keyword, so this is a
//    ham-fisted manner of forcing the issue to minimize function calls.
//    This sometimes makes the library a bit bigger than before, but fast++.
//    However, because they're macros, we need to be SUPER CAREFUL about
//    parameters -- for example, write8(x) may expand to multiple PORT
//    writes that all refer to x, so it needs to be a constant or fixed
//    variable and not something like *ptr++ (which, after macro
//    expansion, may increment the pointer repeatedly and run off into
//    la-la land).  Macros also give us fine-grained control over which
//    operations are inlined on which boards (balancing speed against
//    available program space).

// When using the TFT shield, control and data pins exist in set physical
// locations, but the ports and bitmasks corresponding to each vary among
// boards.  A separate set of pin definitions is given for each supported
// board type.
// When using the TFT breakout board, control pins are configurable but
// the data pins are still fixed -- making every data pin configurable
// would be much too slow.  The data pin layouts are not the same between
// the shield and breakout configurations -- for the latter, pins were
// chosen to keep the tutorial wiring manageable more than making optimal
// use of ports and bitmasks.  So there's a second set of pin definitions
// given for each supported board.

// Shield pin usage:
// LCD Data Bit :    7    6    5    4    3    2    1    0
// Digital pin #:    7    6   13    4   11   10    9    8
// Uno port/pin :  PD7  PD6  PB5  PD4  PB3  PB2  PB1  PB0
// Mega port/pin:  PH4  PH3  PB7  PG5  PB5  PB4  PH6  PH5
// Leo port/pin :  PE6  PD7  PC7  PD4  PB7  PB6  PB5  PB4
// Due port/pin : PC23 PC24 PB27 PC26  PD7 PC29 PC21 PC22

// Breakout pin usage:
// LCD Data Bit :   7   6   5   4   3   2   1   0
// Uno dig. pin :   7   6   5   4   3   2   9   8
// Uno port/pin : PD7 PD6 PD5 PD4 PD3 PD2 PB1 PB0
// Mega dig. pin:  29  28  27  26  25  24  23  22
// Mega port/pin: PA7 PA6 PA5 PA4 PA3 PA2 PA1 PA0 (one contiguous PORT)

// Leo dig. pin :   7   6   5   4   3   2   9   8
// Leo port/pin : PE6 PD7 PC6 PD4 PD0 PD1 PB5 PB4
// Due dig. pin :  40  39  38  37  36  35  34  33
// Due port/pin : PC8 PC7 PC6 PC5 PC4 PC3 PC2 PC1 (one contiguous PORT. -ish…)

// Pixel read operations require a minimum 400 nS delay from RD_ACTIVE
// to polling the input pins.  At 16 MHz, one machine cycle is 62.5 nS.
// This code burns 7 cycles (437.5 nS) doing nothing; the RJMPs are
// equivalent to two NOPs each, final NOP burns the 7th cycle, and the
// last line is a radioactive mutant emoticon.
#define DELAY7        \
  asm volatile(       \
    "rjmp .+0" "\n\t" \
    "rjmp .+0" "\n\t" \
    "rjmp .+0" "\n\t" \
    "nop"      "\n"   \
    ::);

#if defined(__AVR_ATmega168__) || defined(__AVR_ATmega328P__) || defined (__AVR_ATmega328__) || defined(__AVR_ATmega8__)

 // Arduino Uno, Duemilanove, etc.

 #ifdef USE_ADAFRUIT_SHIELD_PINOUT

  // LCD control lines:
  // RD (read), WR (write), CD (command/data), CS (chip select)
  #define RD_PORT PORTC				/*pin A0 */
  #define WR_PORT PORTC				/*pin A1 */
  #define CD_PORT PORTC				/*pin A2 */
  #define CS_PORT PORTC				/*pin A3 */
  #define RD_MASK B00000001
  #define WR_MASK B00000010
  #define CD_MASK B00000100
  #define CS_MASK B00001000

  // These are macros for I/O operations...

  // Write 8-bit value to LCD data lines
  #define write8inline(d) {                          \
    PORTD = (PORTD & B00101111) | ((d) & B11010000); \
    PORTB = (PORTB & B11010000) | ((d) & B00101111); \
    WR_STROBE; } // STROBEs are defined later

  // Read 8-bit value from LCD data lines.  The signle argument
  // is a destination variable; this isn't a function and doesn't
  // return a value in the conventional sense.
  #define read8inline(result) {                       \
    RD_ACTIVE;                                        \
    DELAY7;                                           \
    result = (PIND & B11010000) | (PINB & B00101111); \
    RD_IDLE; }

  // These set the PORT directions as required before the write and read
  // operations.  Because write operations are much more common than reads,
  // the data-reading functions in the library code set the PORT(s) to
  // input before a read, and restore them back to the write state before
  // returning.  This avoids having to set it for output inside every
  // drawing method.  The default state has them initialized for writes.
  #define setWriteDirInline() { DDRD |=  B11010000; DDRB |=  B00101111; }
  #define setReadDirInline()  { DDRD &= ~B11010000; DDRB &= ~B00101111; }

 #else // Uno w/Breakout board

  #define write8inline(d) {                          \
    PORTD = (PORTD & B00000011) | ((d) & B11111100); \
    PORTB = (PORTB & B11111100) | ((d) & B00000011); \
    WR_STROBE; }
  #define read8inline(result) {                       \
    RD_ACTIVE;                                        \
    DELAY7;                                           \
    result = (PIND & B11111100) | (PINB & B00000011); \
    RD_IDLE; }
  #define setWriteDirInline() { DDRD |=  B11111100; DDRB |=  B00000011; }
  #define setReadDirInline()  { DDRD &= ~B11111100; DDRB &= ~B00000011; }

 #endif

  // As part of the inline control, macros reference other macros...if any
  // of these are left undefined, an equivalent function version (non-inline)
  // is declared later.  The Uno has a moderate amount of program space, so
  // only write8() is inlined -- that one provides the most performance
  // benefit, but unfortunately also generates the most bloat.  This is
  // why only certain cases are inlined for each board.
  #define write8 write8inline

#elif defined(__AVR_ATmega1281__) || defined(__AVR_ATmega2561__) || defined(__AVR_ATmega2560__) || defined(__AVR_ATmega1280__) 

 // Arduino Mega, ADK, etc.

 #ifdef USE_ADAFRUIT_SHIELD_PINOUT

  #define RD_PORT PORTF
  #define WR_PORT PORTF
  #define CD_PORT PORTF
  #define CS_PORT PORTF
  #define RD_MASK B00000001
  #define WR_MASK B00000010
  #define CD_MASK B00000100
  #define CS_MASK B00001000

  #define write8inline(d) {                                              \
    PORTH = (PORTH&B10000111)|(((d)&B11000000)>>3)|(((d)&B00000011)<<5); \
    PORTB = (PORTB&B01001111)|(((d)&B00101100)<<2);                      \
    PORTG = (PORTG&B11011111)|(((d)&B00010000)<<1);                      \
    WR_STROBE; }
  #define read8inline(result) {                                      \
    RD_ACTIVE;                                                       \
    DELAY7;                                                          \
    result = ((PINH & B00011000) << 3) | ((PINB & B10110000) >> 2) | \
             ((PING & B00100000) >> 1) | ((PINH & B01100000) >> 5);  \
    RD_IDLE; }
  #define setWriteDirInline() {                                   \
    DDRH |=  B01111000; DDRB |=  B10110000; DDRG |=  B00100000; }
  #define setReadDirInline()  {                                   \
    DDRH &= ~B01111000; DDRB &= ~B10110000; DDRG &= ~B00100000; }

 #else // Mega w/Breakout board
		#define write8inline(d) {\                        
		PORTH &= ~(0x78);\
  	PORTH |= ((d&0xC0) >> 3) | ((d&0x3) << 5);\
  	PORTE &= ~(0x38);\
  	PORTE |= ((d & 0xC) << 2) | ((d & 0x20) >> 2);\
  	PORTG &= ~(0x20);\
  	PORTG |= (d & 0x10) << 1; \ 
    WR_STROBE; }
  #define read8inline(result) { RD_ACTIVE; DELAY7; result = (PINH & 0x60) >> 5;result |= (PINH & 0x18) << 3;result |= (PINE & 0x8) << 2;result |= (PINE & 0x30) >> 2;result |= (PING & 0x20) >> 1;RD_IDLE;}
  #define setWriteDirInline() { DDRH |= 0x78;DDRE |= 0x38;DDRG |= 0x20; }
  #define setReadDirInline()  { DDRH &= ~0x78;DDRE &= ~0x38;DDRG &= ~(0x20); }

		
 #endif

  // All of the functions are inlined on the Arduino Mega.  When using the
  // breakout board, the macro versions aren't appreciably larger than the
  // function equivalents, and they're super simple and fast.  When using
  // the shield, the macros become pretty complicated...but this board has
  // so much code space, the macros are used anyway.  If you need to free
  // up program space, some macros can be removed, at a minor cost in speed.
  #define write8            write8inline
  #define read8             read8inline
  #define setWriteDir       setWriteDirInline
  #define setReadDir        setReadDirInline
  #define writeRegister8    writeRegister8inline
  #define writeRegister16   writeRegister16inline
  #define writeRegisterPair writeRegisterPairInline

#elif defined(__AVR_ATmega32U4__)

 // Arduino Leonardo

 #ifdef USE_ADAFRUIT_SHIELD_PINOUT

  #define RD_PORT PORTF
  #define WR_PORT PORTF
  #define CD_PORT PORTF
  #define CS_PORT PORTF
  #define RD_MASK B10000000
  #define WR_MASK B01000000
  #define CD_MASK B00100000
  #define CS_MASK B00010000

  #define write8inline(d) {                                                   \
    PORTE = (PORTE & B10111111) | (((d) & B10000000)>>1);                     \
    PORTD = (PORTD & B01101111) | (((d) & B01000000)<<1) | ((d) & B00010000); \
    PORTC = (PORTC & B01111111) | (((d) & B00100000)<<2);                     \
    PORTB = (PORTB & B00001111) | (((d) & B00001111)<<4);                     \
    WR_STROBE; }
  #define read8inline(result) {                                      \
    RD_ACTIVE;                                                       \
    DELAY7;                                                          \
    result = ((PINE & B01000000) << 1) | ((PIND & B10000000) >> 1) | \
             ((PINC & B10000000) >> 2) | ((PINB & B11110000) >> 4) | \
              (PIND & B00010000);                                    \
    RD_IDLE; }
  #define setWriteDirInline() {               \
    DDRE |=  B01000000; DDRD |=  B10010000;   \
    DDRC |=  B10000000; DDRB |=  B11110000; }
  #define setReadDirInline() {                \
    DDRE &= ~B01000000; DDRD &= ~B10010000;   \
    DDRC &= ~B10000000; DDRB &= ~B11110000; }

 #else // Leonardo w/Breakout board

  #define write8inline(d) {                                                   \
    uint8_t dr1 = (d) >> 1, dl1 = (d) << 1;                                   \
    PORTE = (PORTE & B10111111) | (dr1 & B01000000);                          \
    PORTD = (PORTD & B01101100) | (dl1 & B10000000) | (((d) & B00001000)>>3) |\
                                  (dr1 & B00000010) |  ((d) & B00010000);     \
    PORTC = (PORTC & B10111111) | (dl1 & B01000000);                          \
    PORTB = (PORTB & B11001111) |(((d) & B00000011)<<4);                      \
    WR_STROBE; }
  #define read8inline(result) {                                       \
    RD_ACTIVE;                                                        \
    DELAY7;                                                           \
    result = (((PINE & B01000000) | (PIND & B00000010)) << 1) |       \
             (((PINC & B01000000) | (PIND & B10000000)) >> 1) |       \
              ((PIND & B00000001) << 3) | ((PINB & B00110000) >> 4) | \
               (PIND & B00010000);                                    \
    RD_IDLE; }
  #define setWriteDirInline() {               \
    DDRE |=  B01000000; DDRD |=  B10010011;   \
    DDRC |=  B01000000; DDRB |=  B00110000; }
  #define setReadDirInline() {                \
    DDRE &= ~B01000000; DDRD &= ~B10010011;   \
    DDRC &= ~B01000000; DDRB &= ~B00110000; }

 #endif

  // On the Leonardo, only the write8() macro is used -- though even that
  // might be excessive given the code size and available program space
  // on this board.  You may need to disable this to get any sizable
  // program to compile.
  #define write8 write8inline
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

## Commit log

2020-03-20 Combined commit
    [Materials.xlsx, apollo01.scad]
2020-03-22 add Arduino source code for valve cycling
2020-03-22 move file in prototype subdirectory
2020-03-22 fix materials
    [Materials.xlsx]
2020-03-22 move .scad file to Drawings
    [apollo01.scad]
2020-03-24 initial set of files with very little progress
    [apollo-ctrl.brd, apollo-ctrl.sch]
2020-04-06 initial files
    [honeywell-mpr-breakout.brd, honeywell-mpr-breakout.sch]
2020-04-07 add FAN support for Prototype v2
2020-04-07 add Gerber/SMTA order info for JLCPCB
    [copper_bottom.gbr, copper_top.gbr, drills.xln, gerber_job.gbrjob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]
2020-04-08 initial drawings
    [bottom bucket.dwg, bottom bucket.dxf]
2020-04-09 photos folder reorg
    [bottom bucket.dwg, honeywell-mpr-breakout.brd, top bucket view.dwg]
2020-04-09 reorg materials/BOM/drawings pdf
    [BOM v2.xlsx, Materials.xlsx]
2020-04-11 code for Arduino use of gasboard7500E, tested and working
2020-04-12 DIY version of PCB sort of done, require review
    [apollo-ctrl.brd, apollo-ctrl.sch]
2020-04-12 bigger PCB preview image
2020-04-12 added more spare pins to i2c header
    [apollo-ctrl.brd, apollo-ctrl.sch]
2020-04-12 fixed wrong battery type
    [apollo-ctrl.brd, apollo-ctrl.sch]
2020-04-12 changed to use Adafruit MPRLS
    [apollo-ctrl.brd, apollo-ctrl.sch]
2020-04-12 added EOC signal to A0
    [apollo-ctrl.brd, apollo-ctrl.sch]
2020-04-12 all components now top side
    [apollo-ctrl.brd, apollo-ctrl.sch]
2020-04-13 added a fan header
    [apollo-ctrl.brd, apollo-ctrl.sch]
2020-04-14 added SPI signals to MPR breakout
    [honeywell-mpr-breakout.brd, honeywell-mpr-breakout.sch]
2020-04-15 MPR 8x mux schematic and PCB
    [mpr-8x-mux.brd, mpr-8x-mux.sch]
2020-04-15 add build instructions prototype v2
2020-04-16 fixed chip select problem with mosfets
    [mpr-8x-mux.brd, mpr-8x-mux.sch]
2020-04-16 added 2x4 header to mpr-8x-mux pcb
    [mpr-8x-mux.brd, mpr-8x-mux.sch]
2020-04-16 minor tweaks for ctrl pcb before fab
    [apollo-ctrl.brd, apollo-ctrl.sch]
2020-04-16 ctrl pcb, more silk text, added extra ADC pins
    [apollo-ctrl.brd, apollo-ctrl.sch]
2020-04-28 add O2 sensor Arduino code, check-in gerbers
    [copper_bottom.gbr, copper_top.gbr, drills.xln, gerber_job.gbrjob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]
2020-04-28 add valve timing code and potentiometer hookup
2020-05-06 add PDF version of building v2 prototype
2020-05-06 add PDF version of building v2 prototype (2)
2020-05-15 add relief valve button
2020-05-17 add motorized valve Arduino code
2020-05-26 added TE MS5837 breakout PCB
    [TE-MS5837-breakout.brd, TE-MS5837-breakout.sch]
2020-05-27 add gerbers to separate directory
    [TE-MS5837-breakout - Copy.csv, TE-MS5837-breakout.brd, TE-MS5837-breakout.csv, copper_bottom.gbr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]
2020-05-27 resize TE board, add mounting holes
    [TE-MS5837-breakout.brd, TE-MS5837-breakout.sch]
2020-05-27 resize MPR board, add mounting holes
    [honeywell-mpr-breakout.brd, honeywell-mpr-breakout.sch]
2020-05-27 move old Gerbers into dedicated directory
    [copper_bottom.gbr, copper_top.gbr, drills.xln, gerber_job.gbrjob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]
2020-05-27 minor fixes (dimensions)
    [TE-MS5837-breakout.brd, honeywell-mpr-breakout.brd]
2020-05-27 add MPR sensor test code
2020-05-27 add ops risk analysis
    [Ops Risk Analysis_Risk Assmt Iss01 (Apollo v01).xlsx]
2020-05-27 add BOM for apollo-ctrl
    [apollo-ctrl-bom-rev20200429.xlsx, apollo-ctrl-bom-rev20200512.xlsx]
2020-05-31 making pressure sensor a lot more reliable
2020-06-02 add needle valve actuator and the MPR pressure together
2020-06-10 add rotary encoder to tweak target pressure
2020-07-10 add some docs
    [O2 concentrator - input pressure calculator.xlsx]
2020-07-11 Apollo v4 control board.docx
2020-07-19 file reorg per prototype
    [BOM v2.xlsx, Materials.xlsx, apollo01.scad, bottom bucket.dwg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]
2020-07-20 prototype v3 reorg
    [BOM v2.xlsx, apollo01.scad, bottom bucket.dwg, bottom bucket.dxf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]
2020-07-28 add various docs
    [Zeolite weight.xlsx]
2020-07-28 new PCB library with ESP32, LCD, and DRV8806
2020-07-29 [Early prototype for refactoring the simulation into a OpenAI gym-compatible API to represent the Apollo MDP][Non-sequential version][Need much more testing]
2020-07-30 template boards
    [Zeolite weight.xlsx, template-apollo.brd, template-apollo.sch]
2020-07-30 new version of template board
    [template-apollo.brd, template-apollo.sch]
2020-07-30 fix template board symbols
    [template-apollo.brd, template-apollo.sch]
2020-07-30 fix template board dimensions
    [template-apollo.brd, template-apollo.sch]
2020-07-30 simulator v1
    [TE-MS5837-breakout - Copy.csv, TE-MS5837-breakout.brd, TE-MS5837-breakout.csv, TE-MS5837-breakout.sch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]
2020-07-30 Created a configurable non blocking state machine for the valve cycle.
2020-07-31 Control valves and concentrator from CLI
2020-07-31 - More CLI commands to configure WIFI and load preferences - CLI hex and binary parser - Moved valve pins - Removed EEPROM delays - Configure button pin
2020-08-01 Added Oxygen Sensor logic
2020-08-02 added support for valve drivers DRV-8806
2020-08-03 move connector bus to the edge of the board
    [template-apollo.brd, template-apollo.sch]
2020-08-05 Initial version of the Apollo V4 modular valve board. No layout, and no header connections, pending pinout decisions with the controller board.
    [valve.sch]
2020-08-05 Added commands to get configuration and sensor data as JSON.
2020-08-06 Show sensor data on display
2020-08-07 Update display with sensor data
2020-08-07 Added BME280 humidity/pressure sensor
2020-08-07 Added Sensor base class
2020-08-08 Added SHTC3 humidity sensor
2020-08-08 Added HDC2080 humidity sensor
2020-08-08 Created sensor manager
2020-08-09 Added CLI humidity sensor support
2020-08-12 Fixed Valve SPI channel conflicting with LCD
2020-08-12 Cleaned up some unnecessary oxygen sensor logic + some small display bug fixes
2020-08-12 Added bar graphs for oxygen and flow
2020-08-12 Update valve board and proposed a pinout for Apollo v4
    [valve.sch]
2020-08-15 Added TCS34725 color sensor
2020-08-15 Drive valves from timer interrupt instrad of main loop to avoid jitter
2020-08-16 Support non automatic Gasboard-7500E oxygen sensors
2020-08-18 PCB experiments
    [NANO33IoTV2.0.brd, NANO33IoTV2.0.sch, experiments.brd, experiments.sch]
2020-08-19 rename Apollo v4 control board.docx -> Apollo v4 control box.docx
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2020-08-24 Start of error infrastructure + color sensor address config
2020-08-28 Initial version of the controller board, ESP32-PICO-KIT edition. Proposed GPIO mapping also updated in the document to break out all otherwise unused pins of the ESP32.
    [ctrl-pico.sch, valve.sch]
2020-08-28 work on error log, sensor errors, error infra
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2020-09-08 - Added CYCLE-DURATIONS command to get/set all durations at once - Additional pressure sensor error check - Increased oxygen sensor sample rate
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2020-09-17 add Apollo v4 docs/presentation for COSMIC meeting
    [experiments-pico.brd, experiments-pico.sch]
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2021-01-29 Update valve board schematic
    [ctrl-pico.sch, valve.sch]
2021-02-08 Remove stepper driver from Valve board to be moved to a future Stepper board
    [valve.sch]
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2021-03-13 Add initial layout for the Valve board. Fully routed, with plenty of room to potentially add the steppers back
    [valve.brd, valve.sch]
2021-03-14 add presentation @hack4good spring 2021
    [Faztek_cap v27.f3d, apollo_sensor_v4.sch]
2021-03-19 Add stepper drivers to the valve board schematic. No guarantee that they fit, but if they do not another board can be made.
    [ctrl-pico.sch, valve.brd, valve.sch]
2021-03-23 Remove the Trinamics bipolar stepper drivers and add unipolar stepper drivers instead (as the motors are cheaper and more available).
    [valve.brd, valve.sch]
2021-03-27 First layout pass for complete valve board
    [valve.brd, valve.sch]
2021-04-01 Clean up valve board silkscreen and change diodes to SOD-123
    [valve.brd, valve.sch]
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2021-04-28 Switch Apollo control board to use discrete SPI LCD and no M5-Stack
    [ctrl-pico.brd, ctrl-pico.sch]
2021-04-28 Add buzzer to Apollo control board and move capacitor away from the USB port
    [ctrl-pico.brd, ctrl-pico.sch]
2021-06-29 add JLCPCB DRU (inspired from OshPark)
    [ctrl-pico.brd]
2021-06-29 DRC error-free
    [ctrl-pico.brd]
2021-07-07 added Gerbers for control board v4 JLCPCB order
    [bom (4).xls, ctrl-pico.GBL, ctrl-pico.GBO, ctrl-pico.GBP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]
2021-09-26 Update TFT LCD pinout for version 2 of the Adafruit breakout board
    [ctrl-pico.brd, ctrl-pico.sch]
2021-09-26 Add touch screen connectors on control PCB, and roll up fab to B
    [ctrl-pico.brd, ctrl-pico.sch]
2021-11-18 disable wifi, sensors and the concentrator to prevent errors on barebone board
2021-11-18 add ESP32-PICO-KIT_V4.1 info
    [BOM_List.xls, ESP32-PICO-KIT-V4.1_0314.DSN, NC_drill.drl]
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2022-08-03 add mic2250
    [mic2250_boost_01-B.Cu.gbl, mic2250_boost_01-B.Mask.gbs, mic2250_boost_01-B.SilkS.gbo, mic2250_boost_01-Edge.Cuts.gm1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]

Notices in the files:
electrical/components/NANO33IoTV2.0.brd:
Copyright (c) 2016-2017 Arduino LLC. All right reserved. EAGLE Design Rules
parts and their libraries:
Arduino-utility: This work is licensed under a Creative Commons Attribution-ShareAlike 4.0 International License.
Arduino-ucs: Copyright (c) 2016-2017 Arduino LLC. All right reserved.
